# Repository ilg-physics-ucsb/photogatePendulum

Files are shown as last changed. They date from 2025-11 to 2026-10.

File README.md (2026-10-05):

# Photogate Pendulum

This repository should hold everything related to the photgates made by the ILG for recording more precise data on a pendulum setup. These photogates were made using off the shelf components from adafruit and amazon and mcmaster using a 3D printed case and a CNC milled PCB. For information on components visit the documentation folder, for information on the case or the ciruit visit the hardware folder and for information on the code visit the code folder. 

## Assembly Instructions

**Materials required** 

* **Integrated Circuits**
* 1x [Adafruit ItsyBitsy M0](https://www.digikey.com/en/products/detail/adafruit-industries-llc/3727/8346575?s=N4IgTCBcDaIIYBM4DMBOBXAlgFwAQ4GcBPXAI0JIFkAGEAXQF8g)
* 1x [LM358 Op Amp DIP-8](https://www.digikey.com/en/products/detail/texas-instruments/LM358P/277042)
* **Transistors**
* 6x [2N3904 NPN BJT](https://www.digikey.com/en/products/detail/diotec-semiconductor/2N3904/13164701)
* 1x [Phototransistor 3mm](https://www.digikey.com/en/products/detail/vishay-semiconductor-opto-division/BPW85A/4071264?s=N4IgTCBcDaIEIAUDqAOArAQRAXQL5A)
* **Diodes**
* 1x [IR LED 5mm](https://www.digikey.com/en/products/detail/vishay-semiconductor-opto-division/TSHF6210/4073549)
* 1x [Blue LED 5mm](https://www.digikey.com/en/products/detail/w%C3%BCrth-elektronik/151051BS04000/4490009)
* 1x [1N4148 Diode](https://www.digikey.com/en/products/detail/onsemi/1N4148/458603)
* **Capacitors**
* 5x [1nF](https://www.digikey.com/en/products/detail/kemet/R82EC1100SH50J/5141859)
* 1x [10nF](https://www.digikey.com/en/products/detail/kemet/R82EC2100AA50J/2571307)
* **Resistors**
* 3x [220Ω](https://www.digikey.com/en/products/detail/stackpole-electronics-inc/CF14JT220R/1741346) 
* 1x [360Ω](https://www.digikey.com/en/products/detail/stackpole-electronics-inc/CF14JT360R/1741406) 
* 1x [1kΩ](https://www.digikey.com/en/products/detail/stackpole-electronics-inc/CF14JT1K00/1741314) 
* 1x [1.2kΩ](https://www.digikey.com/en/products/detail/stackpole-electronics-inc/CF14JT1K20/1741238) 
* 2x [2.2kΩ](https://www.digikey.com/en/products/detail/stackpole-electronics-inc/CF14JT2K20/1741321)
* 9x [10kΩ](https://www.digikey.com/en/products/detail/stackpole-electronics-inc/CF14JT10K0/1741265)
* 2x [22kΩ](https://www.digikey.com/en/products/detail/stackpole-electronics-inc/CF14JT22K0/1741350)
* 1x [33kΩ](https://www.digikey.com/en/products/detail/stackpole-electronics-inc/CF14JT33K0/1741403)
* 2x [47kΩ](https://www.digikey.com/en/products/detail/stackpole-electronics-inc/CF14JT47K0/1741444)
* 3x [100kΩ](https://www.digikey.com/en/products/detail/stackpole-electronics-inc/CF14JT100K/1741263)
* 1x [220kΩ](https://www.digikey.com/en/products/detail/stackpole-electronics-inc/CF14JT220K/1741348)
* 1x [1MΩ](https://www.digikey.com/en/products/detail/stackpole-electronics-inc/CF14JT1M00/1741316) 
* **Tactile**
* 1x [Slide Switch SPDT H6mm](https://www.digikey.com/en/products/detail/same-sky-formerly-cui-devices/SLW-1298856-5A-RA-N-D/24399327)
* **Hardware**
* 1x [FR-1 single sided PCB blank](https://bantamtools.com/products/pcb?variant=32765656432719)
* 1x [1/32th in flat end mill](https://www.mcmaster.com/3066A49)
* 1x [USB-micro to USB-C cable](https://www.amazon.com/Type-C-Fasgear-Braided-Transfer-Compatible/dp/B07CHBR14C/ref=sr_1_3?crid=1D21SSNDEUH8P&dib=eyJ2IjoiMSJ9.PivcPrZAZSg21jQOPEd6xAvt9kDpQqMLWFVfht9Tn8mLNAZzDId2p5OxZ8LkejXtDpPKmn59rHOGYos2S7EBA3ajZcxPJMOG67W7Wv4sRvbQBcF_X5TXTdpQVGO5XpFmnKDs2Iv7MCWgjqrwcuj7gqHg7mUmrMKmFe2VphnZKjZm8xPE3bq8Ao8euvjV_39qhe8JMYmQLRm3Y08NwUTHYXBqhev11vDWwkCIPJ3RTQo.36eqddbM27o5PswbGuCB13i89pmYUmYZE5EW3kyz0KY&dib_tag=se&keywords=usb%2Bc%2Bto%2Busb%2Bmicro%2Bfasgear&qid=1762294692&sprefix=usb%2Bc%2Bto%2Busb%2Bmicro%2Bfasgear%2Caps%2C154&sr=8-3&th=1)
* 5x [M3x10mm screws](https://www.mcmaster.com/91290A115/)
* 5x [M3x6mm threaded inserts](https://www.mcmaster.com/94459A140/)
* 1x [1/4-20x0.226in threaded inserts](https://www.mcmaster.com/94459A736/)
* 1x [6in 1/4-20 mounting rod](https://www.mcmaster.com/97042A268/)

**Creating the PCB**

The heart of the photogate is its PCB housing all of the internal circuitry, all of which is housed on a PCB made to fit the case. All of the schematic and PCB design files can be found in a KiCAD oproject found [here](/Hardware/Circuit/photogatePendulumKiCAD/20AL_Pendulum_Photogate.kicad_pro). You can export the PCB design to a gerber file from here and send to a PCB manufacturer, or the baord has been designed to be able to be milled on a single sided PCB blank. To mill out the PCB you will need to export the edge cuts and bottom layer gerber files and the drill excellon file and then convert these to g-code. There is already a compiled g-code version of the scematic found [here](). This gcode was designed for use on our Bantam desktop milling machine, with a 1/32th in. flat end mill as the cutting tool. In formation on how to use this machine can be found [here](https://gaugeboson.physics.ucsb.edu/wiki/equipment/makerspace/cnc-machine/). Using this machine you can then cut out the PCB from the single sided PCB blank. The following is an image of the final PCB. The PCB May have some rough edges, leftover dust, or the copper may not have come off cleanly so there could be some post processing needed before soldering. You should use scotch brite to rub the surface and sides to get any excess dust and copper bits off. If the edges look rough you may also want to use a de-burring tool on them. 

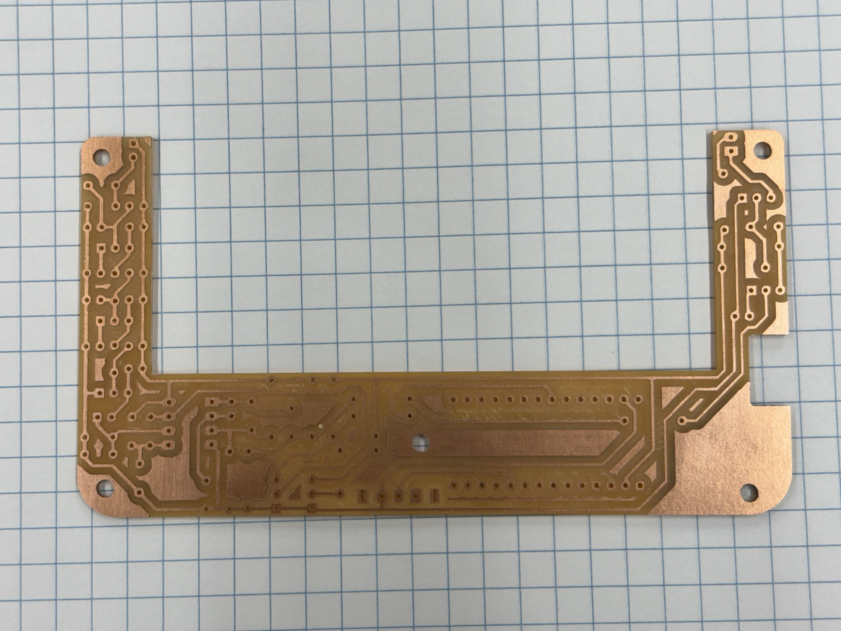
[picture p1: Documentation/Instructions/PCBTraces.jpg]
Result of milling PCB


**Soldering the Circuit**

The components are laid very densly in the PCB and in non standard orientations so here are some directions for how to best get this board together. Before you start soldering also make sure the surface has not tarnished from sitting for too long. If it is tarnished the solder wont stick well, so you will need to buff out the tarnish with some scotch brite before you begin. 

* You should first start [soldering all the components that lay flat](/Documentation/Instructions/SolderFlatComponents.jpg) on the board. These include the 0 ohm resistors (wires) and the horizontally laid resistors. Also make sure to clip the excess leads off of all the components between each step as these will not fit in the case. 

* Next you should put on the [IR LED](/Documentation/Instructions/SolderIRLED.jpg) and [phototransistor](/Documentation/Instructions/SolderPhototransistor.jpg). These sit at a right angle anf flush with the board so you will have to bend them into shape first before soldering. It is very important to get the wires off the back as [flush with the PCB](/Documentation/Instructions/SolderRightAngleParts.jpg) as possible.

* Next the [capacitors should be soldered](/Documentation//Instructions/SolderCapacitors.jpg) in. 

* The switch and the diode should be soldering in next. 

* The [transistors should be soldered in next](/Documentation//Instructions/SolderTransistors.jpg), being careful of which ones are NPN vs PNP as well as which direction they face. 

* Next you should [solder in the last of the reistors](/Documentation//Instructions/SolderUprightResistor.jpg). The transistors already in should make it easier to do this. Parts of the PCB are very desne though so you may still have to clip the leads partway through just to access the rest of the leads you need to solder in. 

* The [8 pin DIP socket comes next](/Documentation//Instructions/SolderIC.jpg), you may need tape to hold it in place though. Make sure that pin 1 is facing the correct direct when installing the socket. 

* Next up is [the Itsy Bitsy](/Documentation//Instructions/SolderItsyBitsy.jpg). The holes for the headers are a bit tight so you should solder the headers onto the itsy bitsy while they are already in the holes on the PCB. 

* Lastly is [the Blue LED](/Documentation//Instructions/SolderBlueLED.jpg). This must be set up above the PCB slightly so that it is flush with the top of the case. 

After you are finished soldering you should plug it in to make sure the photogate works correctly before flashing the code. The Blue LED should light up when the path between the IR LED and phototransistor is obstructed even when there is no code on the teensy. I often forget to install the LM358 into the IC socket so if it is not working first check that. If it is not working and that is not the problem then you should check your solder joints to make sure there isnt any bridging, or for any stray strands of copper leftover from milling. 

**Assembling the Case**

You will also need to 3D print the files for the case, the lid can be found [here](/Hardware//CAD/photogatePendulumLid.stl) and the base [here](/Hardware/CAD/photogatePendulumBase.stl). If you need to edit the case for any reason the raw fusion 360 file can be found [here](/Hardware/CAD/photogatePendulumFusion360.f3z). The file will need supports to print, and we used a 0.1mm layer height and 15% infill with black PLA on a powder coated bed for best results. After the print finishes you will need to remove the supports using pliers from both the bottom and side of the base, and depending on the print quality you may need to clean the print of ant [stringing or stray filament threads](/Documentation/Instructions/FinishedPrint.jpg). 

Now that the print is clean you need to insert all of the interior threaded inserts, these are the M3x6mm inerts. Place them as [shown](/Documentation/Instructions/ThreadedInserts.jpg), and then use a soldering iron to[ heat and push them into place](/Documentation/Instructions/SoldeingThreadedInserts.jpg). As you insert them be careful that they are placed centered on their holes, that they are inserted straight, and that you dont leave any plastic up above the plane they should be flush with. When finished it should look like [this](/Documentation/Instructions/FinalThreadedInserts.jpg). Once the interior threadedinserts are finished you can attached the USB-C to micro-USB cable to the finsished PCB and [place it inside the case](/Documentation/Instructions/ClosingCase.jpg) and screw it together with the M3x10mm screws. 

The last step in assembly is to insert the [1/4-20 threaded insert](/Documentation/Instructions/Quarter20Insert.jpg) for the mounting rod. Since this insert is so large and shallow it is slightly precarious to heat it up with the soldering iron since you cant stick it down the center as you usually would, instaed you need to lay it across the insert and push it down sideways as seen [here](/Documentation/Instructions/SolderingQuarter20.jpg). This process can take some time as the heat transfer is not great, you just should be careful to melt the exterior of the box as little as possible outside the are needed. Once the inser is in s far as it can reasonably go you should [thread in the mounting rod while it is still warm](/Documentation/Instructions/ThreadingMountingRod.jpg) and the plastic is malleable so that the interior plastic forms around the tip giving it a snug fit. 

**Flashing the Code**

The code for this system was made in Arduino IDE and requires the built in libraries to fuction properly, so to flash the code you must use this IDE. The raw .ino file can be found [here](/Code/photogatePendulum/photogatePendulum.ino). To properly compile the code you will also need to install the core for the ItsyBitsy through Arduino IDE, to do this you will need to follow the steps in the ItsyBitsy datasheet. The code also requires a few libraries to work, you can find all of these [here](/Code/Libraries). You will need copy these over into the libraries sub-folder of wherever the Aduino IDE stores its files, often in "~/documents/Arduino/". From here you should be able to compile and upload the code to the ItsyBitsy when it is plugged into your computer.

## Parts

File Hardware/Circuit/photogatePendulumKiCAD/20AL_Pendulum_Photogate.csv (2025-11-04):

Reference | Qty | Value | DNP | Exclude from BOM | Exclude from Board | Footprint | Datasheet
C1,C2,C4,C6,C7 | 5 | 1n |  |  |  | Capacitor_THT:C_Rect_L7.2mm_W2.5mm_P5.00mm_FKS2_FKP2_MKS2_MKP2 | ~
C3 | 1 | 10n |  |  |  | Capacitor_THT:C_Rect_L7.2mm_W2.5mm_P5.00mm_FKS2_FKP2_MKS2_MKP2 | ~
C5 | 1 | 4n7 |  |  |  | Capacitor_THT:C_Rect_L7.2mm_W2.5mm_P5.00mm_FKS2_FKP2_MKS2_MKP2 | ~
D1 | 1 | LED IR |  |  |  | LED_THT:LED_D5.0mm_Horizontal_O3.81mm_Z3.0mm | ~
D2 | 1 | 1N4148 |  |  |  | Diode_THT:D_DO-35_SOD27_P2.54mm_Vertical_AnodeUp | https://assets.nexperia.com/documents/data-sheet/1N4148_1N4448.pdf
D3 | 1 | LED RED |  |  |  | LED_THT:LED_D5.0mm_Clear | ~
Q1 | 1 | 2N3906 |  |  |  | Package_TO_SOT_THT:TO-92_Inline_Wide | https://www.onsemi.com/pub/Collateral/2N3906-D.PDF
Q2,Q3,Q5,Q6,Q7,Q8 | 6 | 2N3904 |  |  |  | Package_TO_SOT_THT:TO-92_Inline_Wide | https://www.onsemi.com/pub/Collateral/2N3903-D.PDF
Q4 | 1 | BPW40 |  |  |  | LED_THT:LED_D3.0mm_Horizontal_O3.81mm_Z2.0mm | https://www.rcscomponents.kiev.ua/datasheets/bpw40.pdf
R1,R13 | 2 | 2k2 |  |  |  | Resistor_THT:R_Axial_DIN0207_L6.3mm_D2.5mm_P2.54mm_Vertical | ~
R2,R3,R7,R8,R20 | 5 | 10k |  |  |  | Resistor_THT:R_Axial_DIN0207_L6.3mm_D2.5mm_P10.16mm_Horizontal | ~
R4 | 1 | 10k |  |  |  | Resistor_THT:R_Axial_DIN0207_L6.3mm_D2.5mm_P5.08mm_Vertical | ~
R5 | 1 | 1k3 |  |  |  | Resistor_THT:R_Axial_DIN0207_L6.3mm_D2.5mm_P2.54mm_Vertical | ~
R6 | 1 | 22k |  |  |  | Resistor_THT:R_Axial_DIN0207_L6.3mm_D2.5mm_P10.16mm_Horizontal | ~
R9 | 1 | 220 |  |  |  | Resistor_THT:R_Axial_DIN0207_L6.3mm_D2.5mm_P10.16mm_Horizontal | ~
R10 | 1 | 360 |  |  |  | Resistor_THT:R_Axial_DIN0207_L6.3mm_D2.5mm_P5.08mm_Vertical | ~
R11 | 1 | 22k |  |  |  | Resistor_THT:R_Axial_DIN0207_L6.3mm_D2.5mm_P2.54mm_Vertical | ~
R12,R14,R26 | 3 | 10k |  |  |  | Resistor_THT:R_Axial_DIN0207_L6.3mm_D2.5mm_P2.54mm_Vertical | ~
R15 | 1 | 100k |  |  |  | Resistor_THT:R_Axial_DIN0207_L6.3mm_D2.5mm_P5.08mm_Vertical | ~
R16,R17 | 2 | 47k |  |  |  | Resistor_THT:R_Axial_DIN0207_L6.3mm_D2.5mm_P5.08mm_Vertical | ~
R18 | 1 | 33k |  |  |  | Resistor_THT:R_Axial_DIN0207_L6.3mm_D2.5mm_P5.08mm_Vertical | ~
R19 | 1 | 220 |  |  |  | Resistor_THT:R_Axial_DIN0207_L6.3mm_D2.5mm_P7.62mm_Horizontal | ~
R21 | 1 | 100k |  |  |  | Resistor_THT:R_Axial_DIN0207_L6.3mm_D2.5mm_P7.62mm_Horizontal | ~
R22,R29,R30,R31 | 4 | 0 |  |  |  | Resistor_THT:R_Axial_DIN0207_L6.3mm_D2.5mm_P10.16mm_Horizontal | ~
R23 | 1 | 220 |  |  |  | Resistor_THT:R_Axial_DIN0207_L6.3mm_D2.5mm_P2.54mm_Vertical | ~
R24 | 1 | 220k |  |  |  | Resistor_THT:R_Axial_DIN0207_L6.3mm_D2.5mm_P2.54mm_Vertical | ~
R25 | 1 | 100k |  |  |  | Resistor_THT:R_Axial_DIN0207_L6.3mm_D2.5mm_P2.54mm_Vertical | ~
R27 | 1 | 1k |  |  |  | Resistor_THT:R_Axial_DIN0207_L6.3mm_D2.5mm_P2.54mm_Vertical | ~
R28 | 1 | 1M |  |  |  | Resistor_THT:R_Axial_DIN0207_L6.3mm_D2.5mm_P2.54mm_Vertical | ~
SW2 | 1 | SW_SPDT |  |  |  | User:SlideSwitch_SPDT | ~
U1 | 1 | ~ |  |  |  | User:AdafruitItsyBitsyM0
U2 | 1 | LM358 |  |  |  | Package_DIP:DIP-8_W7.62mm_Socket_LongPads | http://www.ti.com/lit/ds/symlink/lm2904-n.pdf

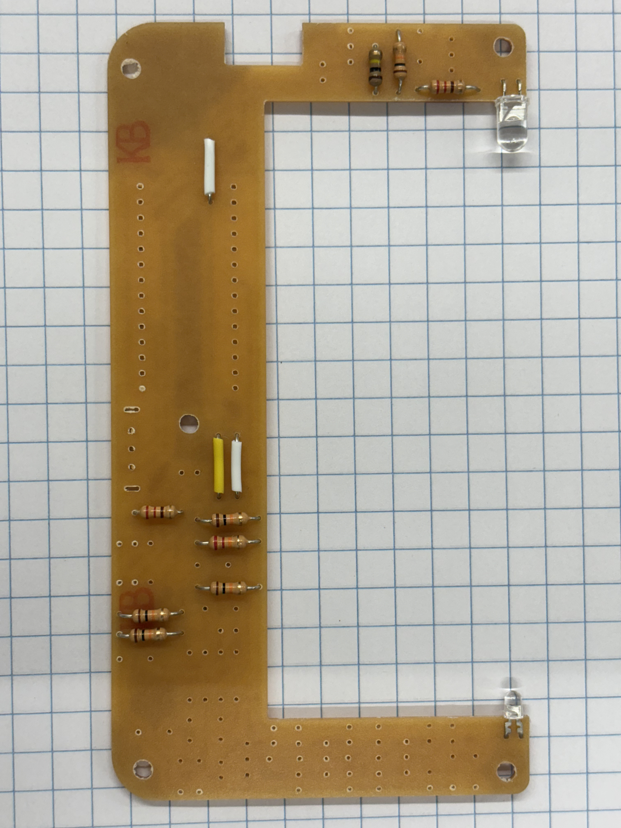
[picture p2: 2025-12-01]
Documentation/Instructions/SolderRightAngleParts.jpg

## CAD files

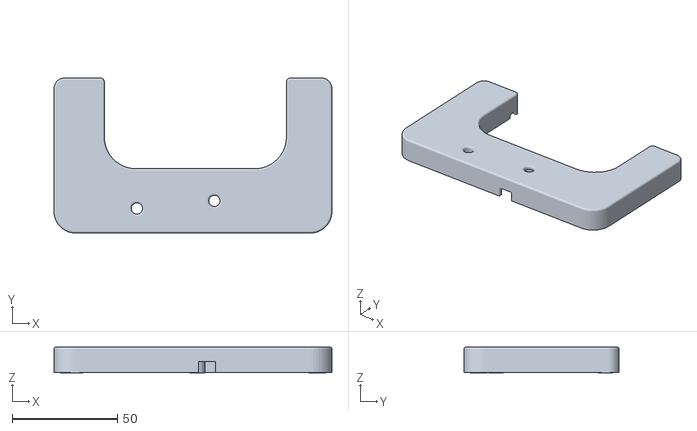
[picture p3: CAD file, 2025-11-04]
Hardware/CAD/photogatePendulumLid.stl
132.2 x 73.8 x 12.3

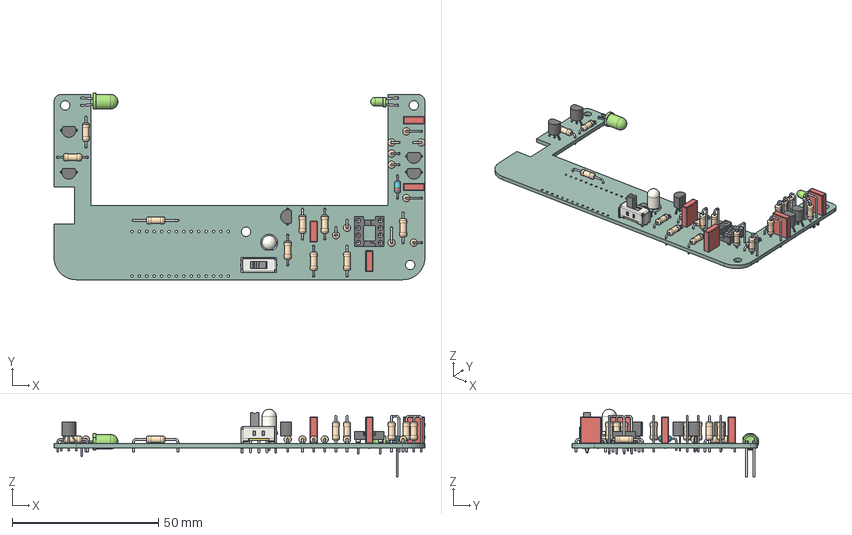
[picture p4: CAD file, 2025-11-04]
Hardware/Circuit/photogatePendulumKiCAD/20AL_Pendulum_Photogate.step
127.0 x 63.9 x 23.1 mm
R_Axial_DIN0207_L6.3mm_D2.5mm_P10.16mm_Horizontal x 8
R_Axial_DIN0207_L6.3mm_D2.5mm_P2.54mm_Vertical x 7
TO-92_Inline_Wide x 5
SW_Slide_SPDT_Straight_CK_OS102011MS2Q
LED_D5.0mm_Horizontal_O3.81mm_Z3.0mm
R_Axial_DIN0207_L6.3mm_D2.5mm_P5.08mm_Vertical x 3
DIP-8_W7.62mm_Socket
C_Rect_L7.2mm_W2.5mm_P5.00mm_FKS2_FKP2_MKS2_MKP2 x 4
LED_D3.0mm_Horizontal_O3.81mm_Z10.0mm
R_Axial_DIN0207_L6.3mm_D2.5mm_P15.24mm_Horizontal
LED_D5.0mm_Clear
D_DO-35_SOD27_P7.62mm_Horizontal
20AL_Pendulum_Photogate_PCB

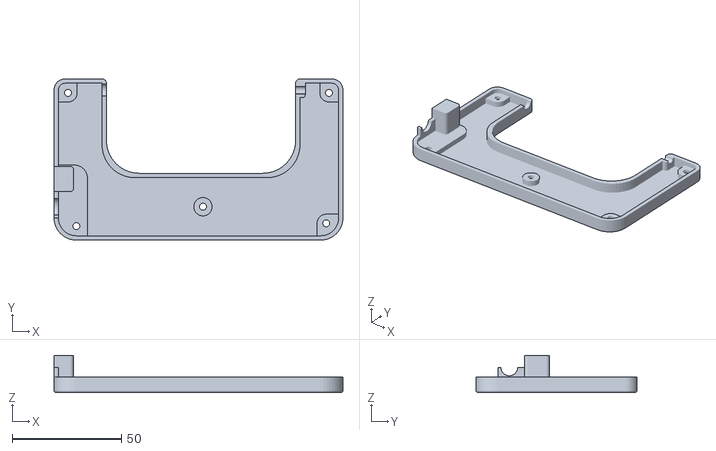
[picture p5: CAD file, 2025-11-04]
Hardware/CAD/photogatePendulumBase.stl
132.2 x 73.8 x 17.1

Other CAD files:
Hardware/CAD/photogatePendulumFusion360.f3z

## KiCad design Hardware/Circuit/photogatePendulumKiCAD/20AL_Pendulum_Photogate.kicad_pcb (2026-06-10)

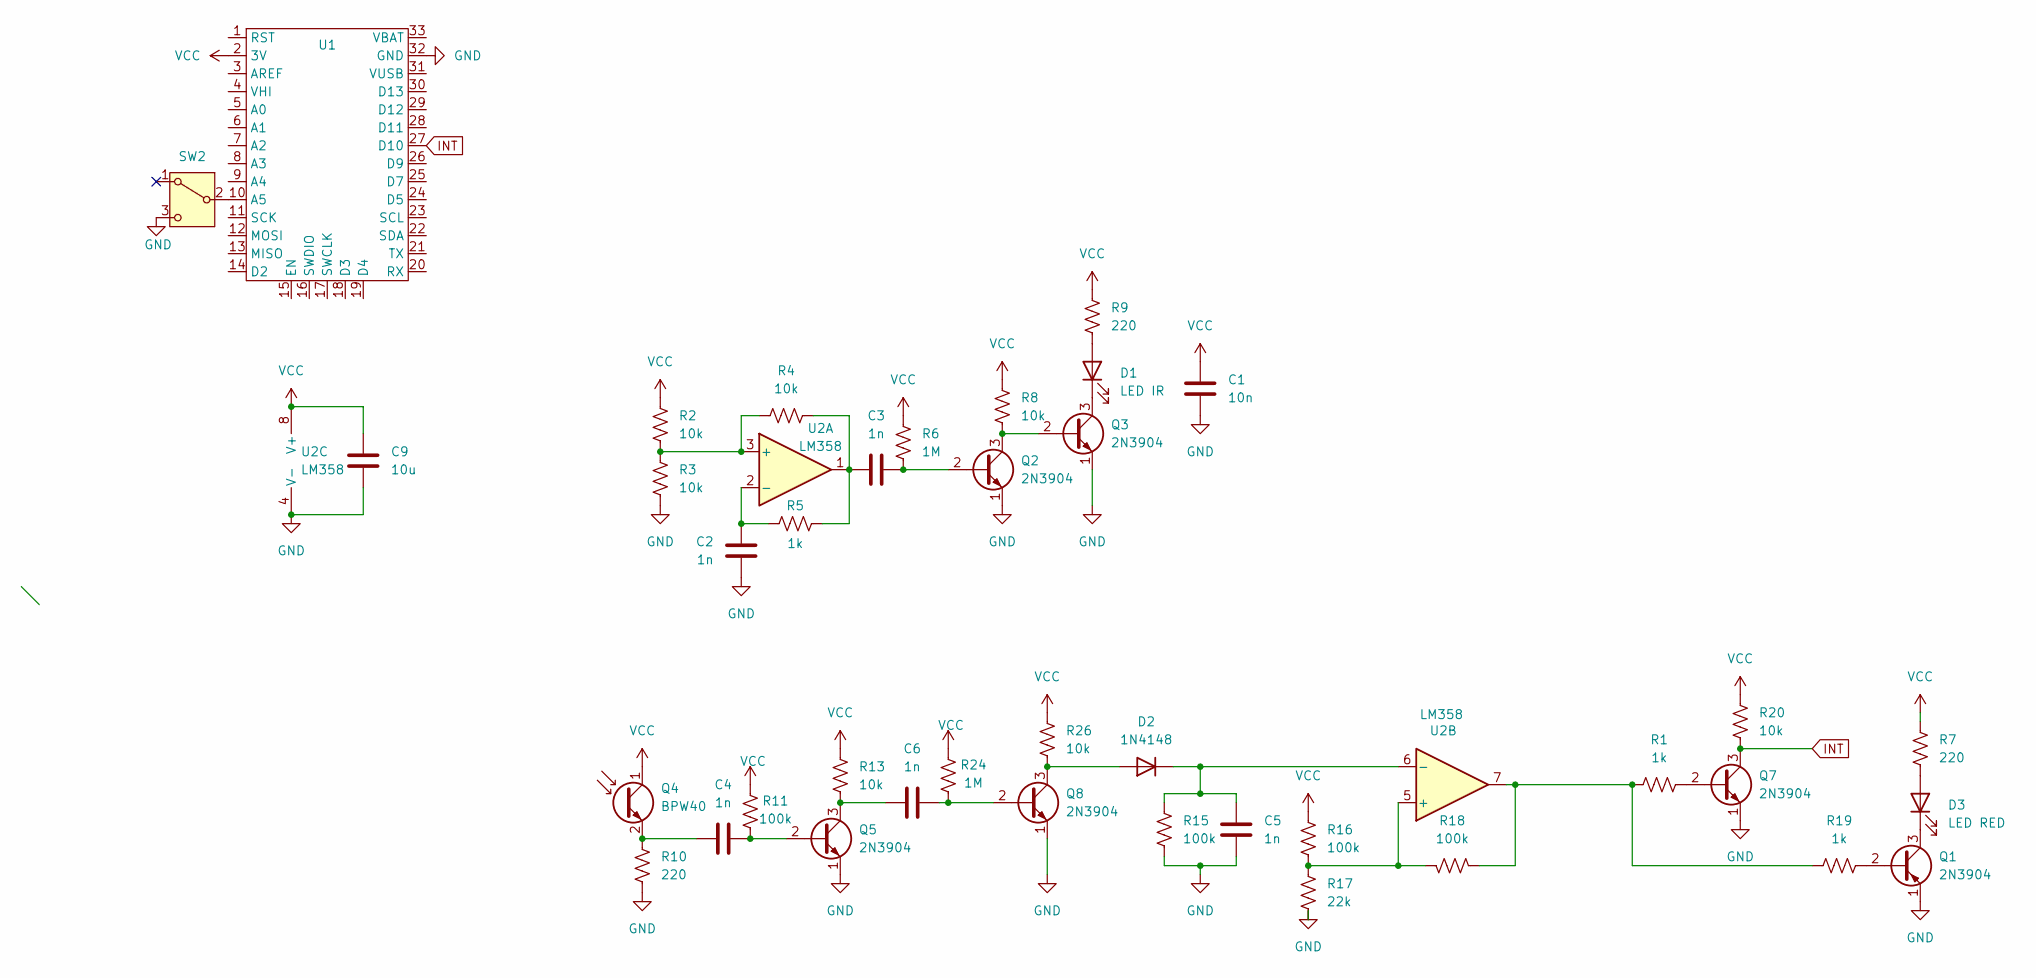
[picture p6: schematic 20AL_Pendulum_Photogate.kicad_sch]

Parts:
C1: 10n; C_Rect_L7.2mm_W2.5mm_P5.00mm_FKS2_FKP2_MKS2_MKP2
C2, C3, C4, C5, C6: 1n; C_Rect_L7.2mm_W2.5mm_P5.00mm_FKS2_FKP2_MKS2_MKP2
C9: 10u; C_Rect_L7.2mm_W2.5mm_P5.00mm_FKS2_FKP2_MKS2_MKP2
D1: LED IR; LED_D5.0mm_Horizontal_O3.81mm_Z3.0mm
D2: 1N4148; D_DO-35_SOD27_P7.62mm_Horizontal
D3: LED RED; LED_D5.0mm_Clear
Q1, Q2, Q3, Q5, Q7, Q8: 2N3904; TO-92_Inline_Wide
Q4: BPW40; LED_D3.0mm_Horizontal_O3.81mm_Z2.0mm
R1, R5: 1k; R_Axial_DIN0207_L6.3mm_D2.5mm_P7.62mm_Horizontal
R2: 10k; R_Axial_DIN0207_L6.3mm_D2.5mm_P10.16mm_Horizontal
R3, R4, R8, R13, R26: 10k; R_Axial_DIN0207_L6.3mm_D2.5mm_P7.62mm_Horizontal
R6, R24: 1M; R_Axial_DIN0207_L6.3mm_D2.5mm_P7.62mm_Horizontal
R7, R9: 220; R_Axial_DIN0207_L6.3mm_D2.5mm_P10.16mm_Horizontal
R10: 220; R_Axial_DIN0207_L6.3mm_D2.5mm_P7.62mm_Horizontal
R11, R15, R16, R18: 100k; R_Axial_DIN0207_L6.3mm_D2.5mm_P7.62mm_Horizontal
R17: 22k; R_Axial_DIN0207_L6.3mm_D2.5mm_P7.62mm_Horizontal
R19: 1k; R_Axial_DIN0207_L6.3mm_D2.5mm_P10.16mm_Horizontal
R20: 10k; R_Axial_DIN0207_L6.3mm_D2.5mm_P15.24mm_Horizontal
SW2: SW_SPDT; SlideSwitch_SPDT
U1: AdafruitItsyBitsyM0
U2: LM358; DIP-8_W7.62mm_Socket_LongPads

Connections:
GND: C1.1, C2.2, C5.1, C9.2, Q1.1 (E), Q2.1 (E), Q3.1 (E), Q5.1 (E), Q7.1 (E), Q8.1 (E), R3.2, R10.2, R15.2, R17.2, SW2.3 (C), U1.32 (GND), U2.4 (V-)
INT: Q7.3 (C), R20.2, U1.27 (D10)
unnamed: C3.1, R4.2, R5.2, U2.1
unnamed: D1.2 (A), R9.2
unnamed: D1.1 (K), Q3.3 (C)
unnamed: D2.2 (A), Q8.3 (C), R26.2
unnamed: C5.2, D2.1 (K), R15.1, U2.6 (-)
unnamed: D3.2 (A), R7.1
unnamed: D3.1 (K), Q1.3 (C)
unnamed: Q1.2 (B), R19.2
unnamed: C3.2, Q2.2 (B), R6.2
unnamed: Q2.3 (C), Q3.2 (B), R8.2
unnamed: C4.1, Q4.2 (E), R10.1
unnamed: C4.2, Q5.2 (B), R11.2
unnamed: C6.1, Q5.3 (C), R13.2
unnamed: Q7.2 (B), R1.2
unnamed: C6.2, Q8.2 (B), R24.2
unnamed: R1.1, R18.2, R19.1, U2.7
unnamed: SW2.2 (B), U1.10 (A5)
unnamed: R2.2, R3.1, R4.1, U2.3 (+)
unnamed: C2.1, R5.1, U2.2 (-)
unnamed: R16.1, R17.1, R18.1, U2.5 (+)
VCC: C1.2, C9.1, Q4.1 (C), R2.1, R6.1, R7.2, R8.1, R9.1, R11.1, R13.1, R16.2, R20.1, R24.1, R26.1, U1.2 (3V), U2.8 (V+)

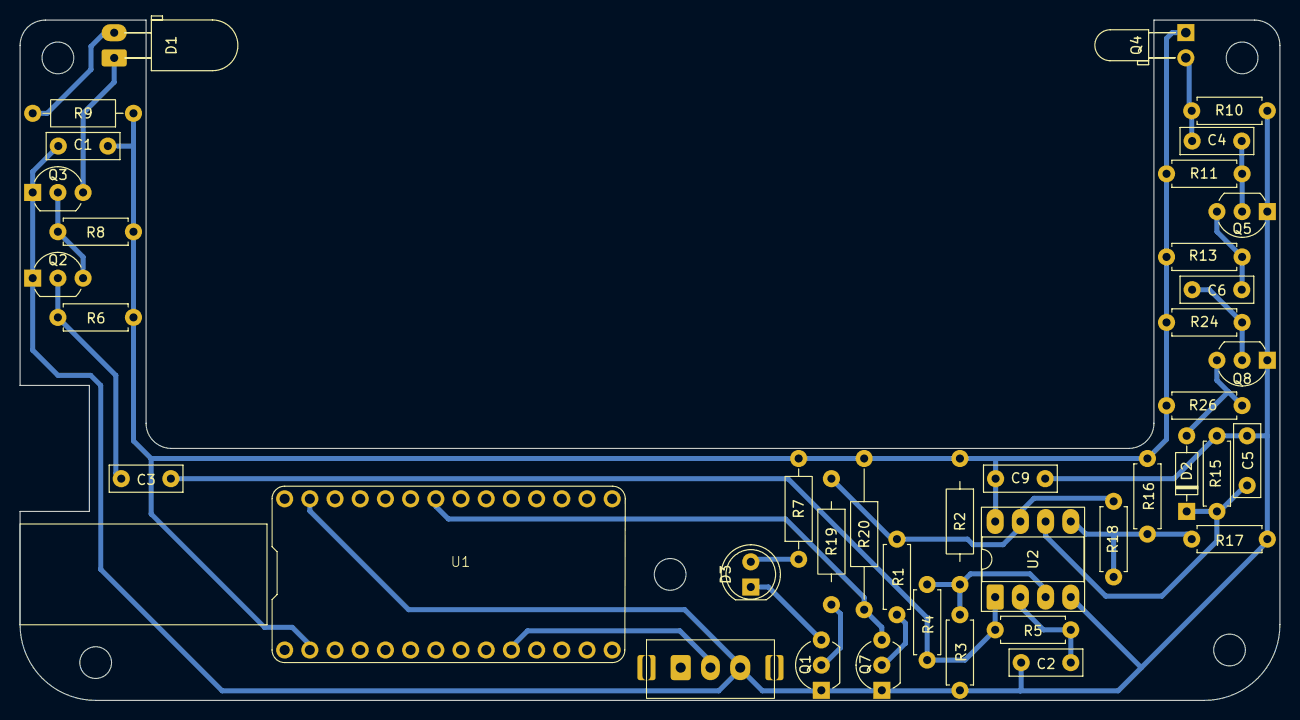
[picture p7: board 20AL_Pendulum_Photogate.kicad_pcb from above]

Board: 2 copper layers, 127.0 x 68.6 mm, 40 parts (0 on the bottom side), 23 nets.

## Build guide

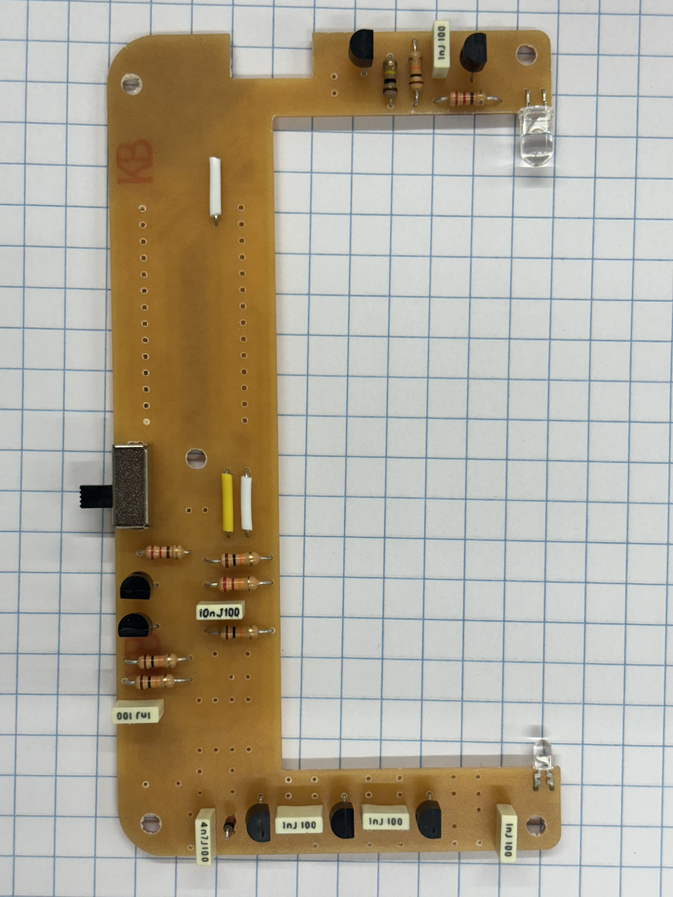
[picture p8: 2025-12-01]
Documentation/Instructions/SolderTransistors.jpg

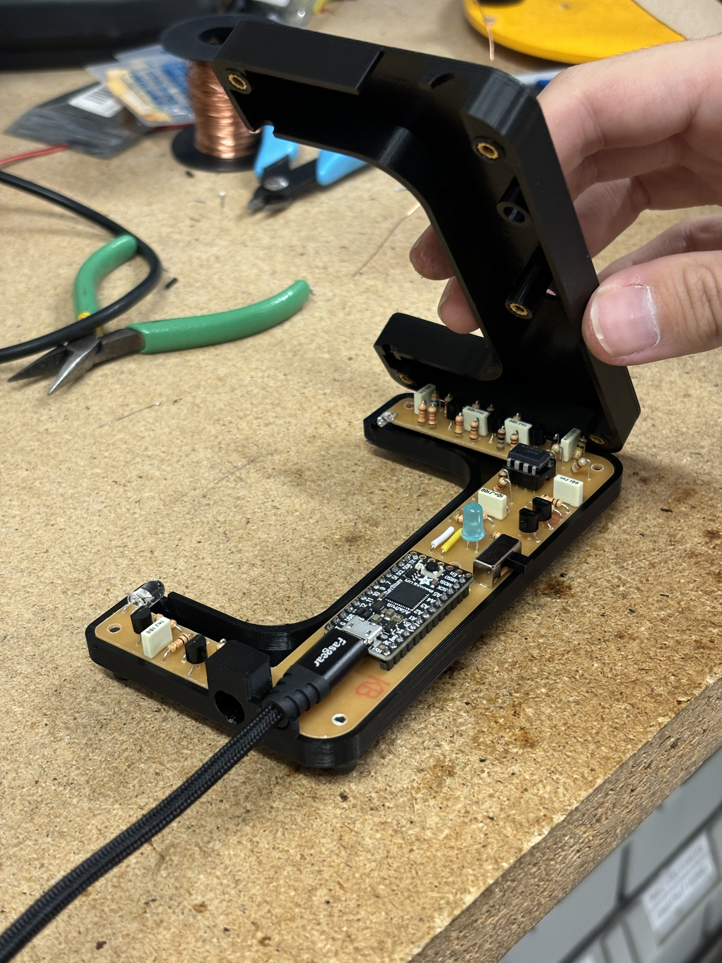
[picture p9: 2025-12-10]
Documentation/Instructions/ClosingCase.jpg

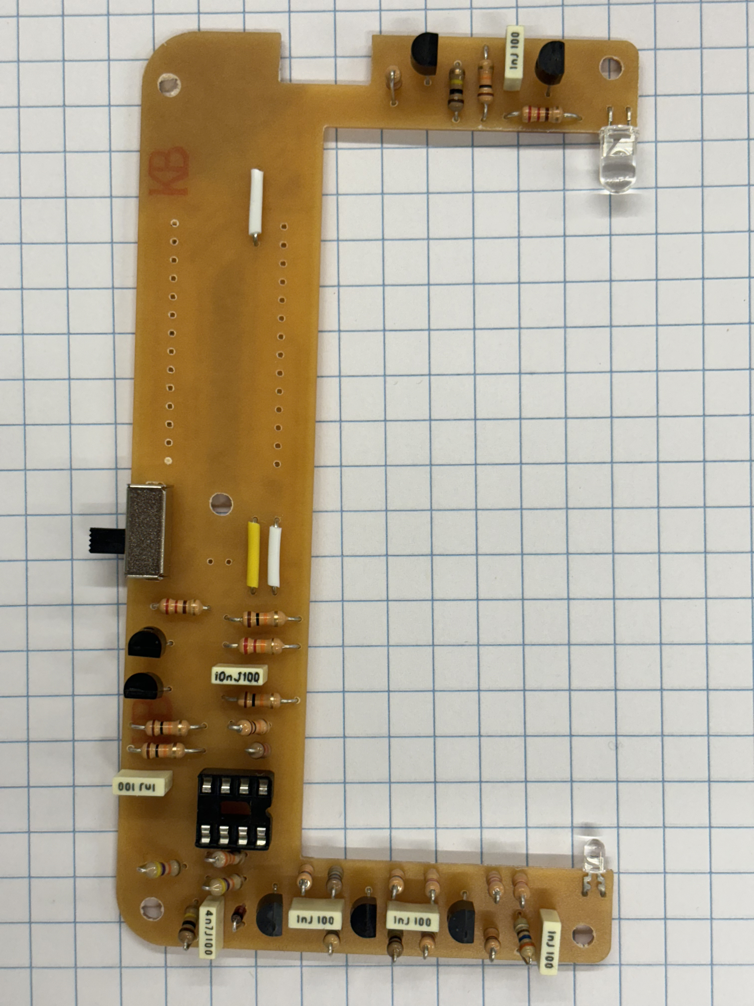
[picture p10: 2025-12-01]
Documentation/Instructions/SolderIC.jpg

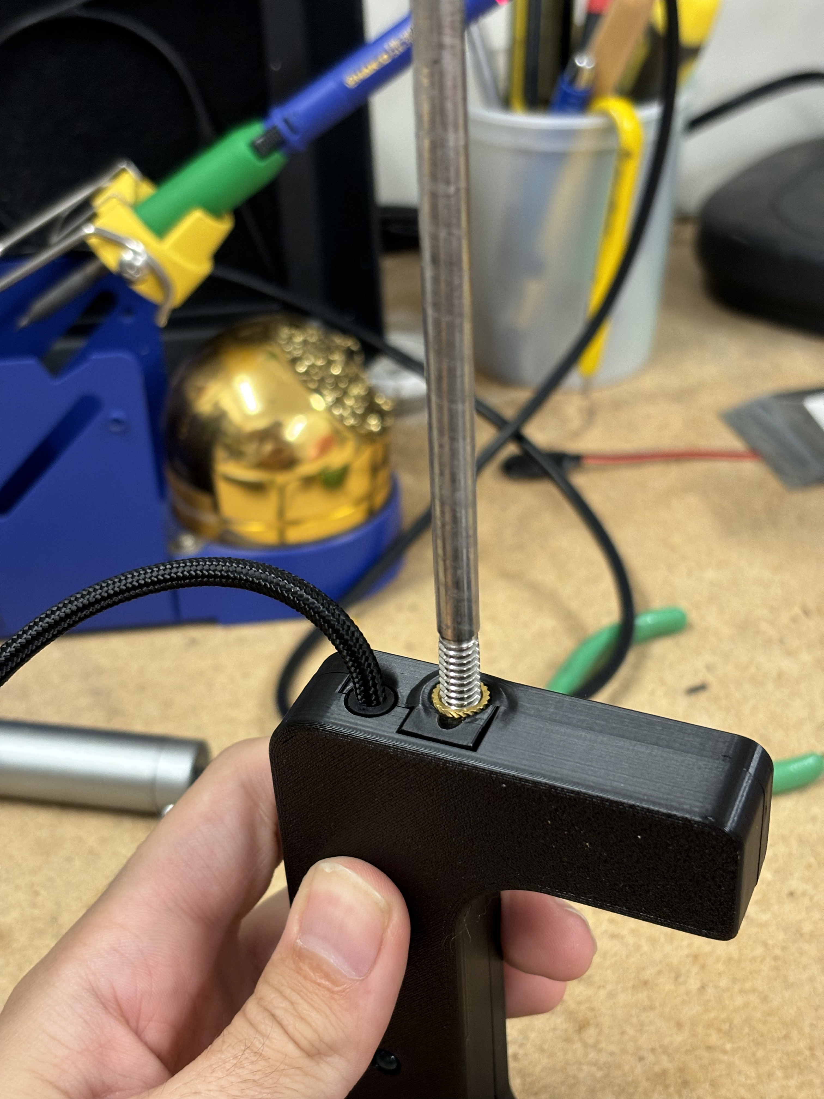
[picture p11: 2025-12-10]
Documentation/Instructions/ThreadingMountingRod.jpg

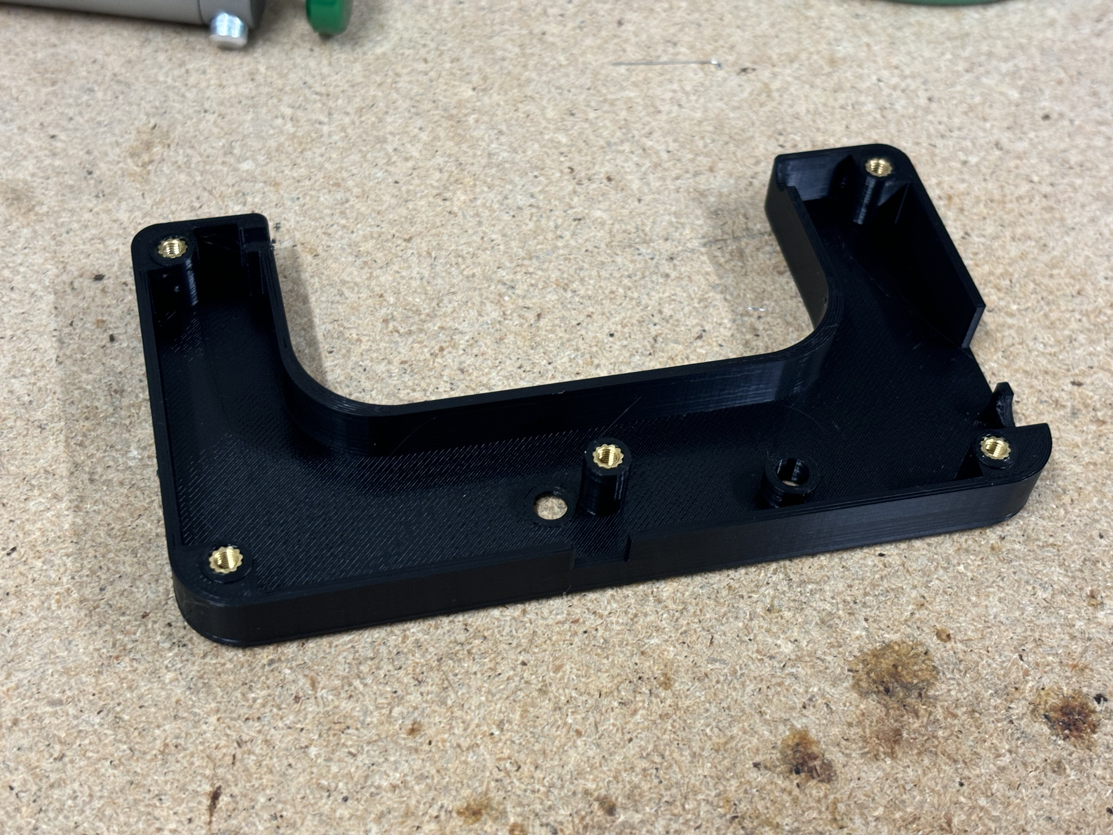
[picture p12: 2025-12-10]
Documentation/Instructions/FinalThreadedInserts.jpg

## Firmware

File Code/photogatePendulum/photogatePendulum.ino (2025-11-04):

#include <Keyboard.h>
#include <Adafruit_DotStar.h>

#define PIN_BUTTON 7
#define PIN_PHOTOGATE 10
#define PIN_SWITCH A5

Adafruit_DotStar onBoardLED(DOTSTAR_NUM, PIN_DOTSTAR_DATA, PIN_DOTSTAR_CLK, DOTSTAR_BRG);

uint32_t debounceTimer = 50 ;
char timeBuff[7] ;
float time = 0 ;
float timeDel = 0 ;

bool buttonState = 0 ;
bool buttonStateLast = 0 ;
uint32_t buttonTimer = 0 ;

bool switchState = 0 ;
bool switchStateLast = 0 ;
uint32_t switchTimer = 0 ;

uint64_t photogateTimeLeading = 0 ;
uint64_t photogateTimeFollow = 0 ;
bool photogateFlag = 0 ;

void interruptPhotogate(){
  if (!digitalRead(PIN_PHOTOGATE)){
    photogateTimeLeading = micros() ;
  } else {
    photogateTimeFollow = micros() ;
    photogateFlag = 1 ;
  }
}

void setup() {
  // Init on Board LED
  onBoardLED.begin(); // Initialize pins for output
  onBoardLED.setBrightness(80);
  onBoardLED.show();  // Turn all LEDs off ASAP

  pinMode(PIN_BUTTON, INPUT_PULLUP) ;
  pinMode(PIN_SWITCH, INPUT_PULLUP) ;
  pinMode(PIN_PHOTOGATE, INPUT) ;
  attachInterrupt(PIN_PHOTOGATE, interruptPhotogate, CHANGE) ;

  // Init communication methods
  Serial.begin(115200) ;
  delay(500) ;
  Serial.println("Started software") ;
  Keyboard.begin() ;

  // Init Switch
  switchStateLast = switchState ;
  if (switchState){
    // What to do when switch turned on
    onBoardLED.setPixelColor(0, 255, 0, 0) ; // Show the program through the LEDs
    onBoardLED.show();
  } else {
    // What to do when switch turned off
    onBoardLED.setPixelColor(0, 0, 255, 0) ; // Show the program through the LEDs
    onBoardLED.show();
  }
}

void loop() {  

  // Run on state change of switch
  switchState = digitalRead(PIN_SWITCH) ;
  if ( (switchState != switchStateLast) && (millis() - switchTimer >= debounceTimer) ){
    switchTimer = millis() ;
    switchStateLast = switchState ;

    Serial.println(switchState) ;

    if (switchState){
      // What to do when switch turned on
      onBoardLED.setPixelColor(0, 255, 0, 0) ; // Show the program through the LEDs
      onBoardLED.show();
    } else {
      // What to do when switch turned off
      onBoardLED.setPixelColor(0, 0, 255, 0) ; // Show the program through the LEDs
      onBoardLED.show();
    }
  }

  // Run on photogate trigger
  if (photogateFlag){
    photogateFlag = 0 ;
    time = (float) photogateTimeLeading/1000000 ;
    timeDel = (float) (photogateTimeFollow - photogateTimeLeading)/1000000 ;
    if (switchState){
      Keyboard.print(time, 4) ;
      delay(10) ;
      Keyboard.print("\t") ;
      delay(10) ;
      Keyboard.println(timeDel, 6) ;
    }
  }

}

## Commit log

2025-11-04 Init the repo
    [20AL_Pendulum_Photogate.kicad_pcb, 20AL_Pendulum_Photogate.kicad_sch, 20AL_Pendulum_Photogate.step, photogatePendulumBase.stl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]
2025-11-04 Start materials list
    [20AL_Pendulum_Photogate.csv]
2025-11-20 Add soldering to readme
2025-12-01 Add instruction Pictures
    [20AL_Pendulum_Photogate-B_Cu.gbr, 20AL_Pendulum_Photogate-Edge_Cuts.gbr, 20AL_Pendulum_Photogate-drl_map.gbr, 20AL_Pendulum_Photogate-job.gbrjob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]
2026-06-10 Finalize design
    [20AL_Pendulum_Photogate-B_Cu.gbr, 20AL_Pendulum_Photogate-B_Mask.gbr, 20AL_Pendulum_Photogate-B_Paste.gbr, 20AL_Pendulum_Photogate-B_Silkscreen.gbr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]
